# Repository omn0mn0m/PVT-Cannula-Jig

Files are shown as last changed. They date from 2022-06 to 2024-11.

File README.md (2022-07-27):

# Needle-Holster
For creating cannulas

Design for cannula holster was coded by medical student Nam Tran in the program OpenSCAD with a base width and depth of 20mm and diamond shaped wells with a diameter of 0.5mm and a depth of 2.3mm. 

## Usage
Modifications can be done to `Holster.scad` using the OpenSCAD software by either editing the variables in code or using the Customizer window.

To modify and print, follow these general steps:

1. Make modifications in OpenSCAD and save.
2. Click "Render" (F6).
3. Click "Export as STL" (F7).
4. Slice the STL file into gcode using either [Cura](https://ultimaker.com/software/ultimaker-cura), [Slic3r](https://slic3r.org/), or some other slicing software.

### Test Print
An initial test print should be done using a `wells_per_row` of 1 and a `wells_per_column` of 1. This is to ensure the least amount of plastic waste.

### Quality Assessment
The print should be assessed for quality, ensuring all layers of the print were uniform and that a 26G barrel could enter the wells with ease.

In the case that adjustment is needed, bed levelling, bed and nozzle temperature adjustment, and making sure that the belts of the printer are properly tightened can improve print quality. Common troubleshooting steps can be found [here](https://www.simplify3d.com/support/print-quality-troubleshooting/) for various print quality issues.

### Measurement Assessment
Well depth can be assessed using digital calipers to measure the base of the holster, the length of a barrel, and the total length of the barrel inserted fully into each well in order to determine that 2.3mm of barrel was concealed.

In the case that adjustment is needed, `depth_tolerance` and `diameter_tolerance` can be adjusted in increments of 0.1mm. Anecdotally, the diameter tolerance should usually be set to the 3D printer nozzle width (e.g. 0.4mm).

### Post-Print Modification
In the event that the wells are still shallow, a 26G needle can be inserted into the well, applying pressure with a twisting motion to further carve out the well to the desired depth.

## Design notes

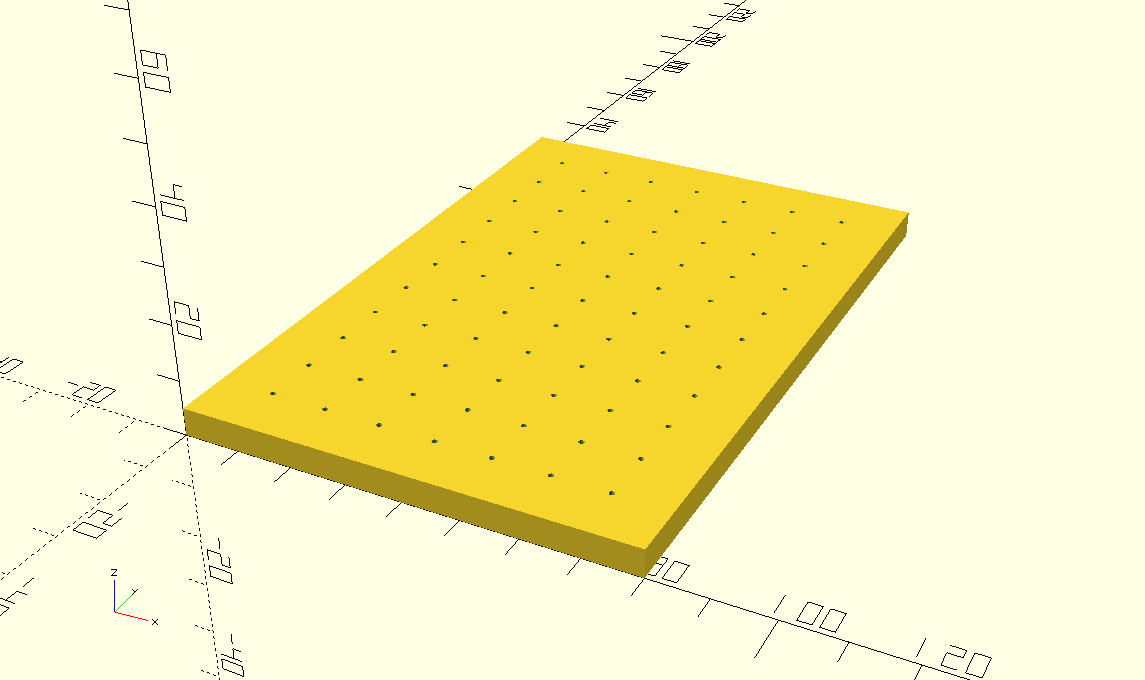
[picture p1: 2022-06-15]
Holster.png

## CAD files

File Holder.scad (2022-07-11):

/**
Title: Needle Holder
Description: Holder for 24ga needles
Designer: Nam Tran
Units: mm
Last Modified: 2022-07-10
*/

well_depth = 2.3;
depth_tolerance = 0.0;
well_diameter = 0.5;
diameter_tolerance = 0.0;
distance_between_wells = 10.0;

wells_per_row = 4;
wells_per_column = 2;
base_height = 5.0;

module base() {
    cube([((wells_per_row + 1) * distance_between_wells), ((wells_per_column + 1) * distance_between_wells), base_height]);
}

module wells() {
    for (i = [0:(wells_per_row - 1)]) {
        for (j = [0:(wells_per_column - 1)]) {
            translate([distance_between_wells+(distance_between_wells * i), distance_between_wells+(distance_between_wells * j), (base_height - well_depth)])
            //cylinder(h=(well_depth + 0.1), r=well_diameter, $fn=360);
            cube([(well_diameter + diameter_tolerance), (well_diameter + diameter_tolerance), (well_depth + depth_tolerance + 0.1)]);
        }
    }
}

difference() {
    base();
    wells();
}

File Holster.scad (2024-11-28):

/**
Title: Needle Holder
Description: Holder for 24ga needles
Designer: Nam Tran
Units: mm
Last Modified: 2022-07-10
*/

/*[ Well Values] */
well_depth = 0.6; // .1
// Depth adjustment from "true" value
depth_tolerance = 0.0; // .1
well_diameter = 0.5; // .1
// Diameter adjustment from "true" value
diameter_tolerance = 0.0; // .1

/* [Base Values] */
wells_per_row = 4; // [1:10]
wells_per_column = 2; // [1:10]
distance_between_wells = 10.0; // .1
base_height = 5.0; // .1

module base() {
    cube([((wells_per_row + 1) * distance_between_wells), ((wells_per_column + 1) * distance_between_wells), base_height]);
}

module wells() {
    for (i = [0:(wells_per_row - 1)]) {
        for (j = [0:(wells_per_column - 1)]) {
            translate([distance_between_wells+(distance_between_wells * i), distance_between_wells+(distance_between_wells * j), (base_height - well_depth)])
            //cylinder(h=(well_depth + 0.1), r=well_diameter, $fn=360);
            cube([(well_diameter + diameter_tolerance), (well_diameter + diameter_tolerance), (well_depth + depth_tolerance + 0.1)]);
        }
    }
}

difference() {
    base();
    wells();
}

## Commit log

2022-06-16 Changed round holes to square holes
    [Holder.scad]
2022-07-11 Added gitignore and changed up some variables
    [Holder.scad]
2022-07-11 Sensible defaults
    [Holder.scad]
2022-07-27 Some more modifications + instructions
    [Holster.scad]
2024-11-28 Updated scad file
    [Holster.scad]
